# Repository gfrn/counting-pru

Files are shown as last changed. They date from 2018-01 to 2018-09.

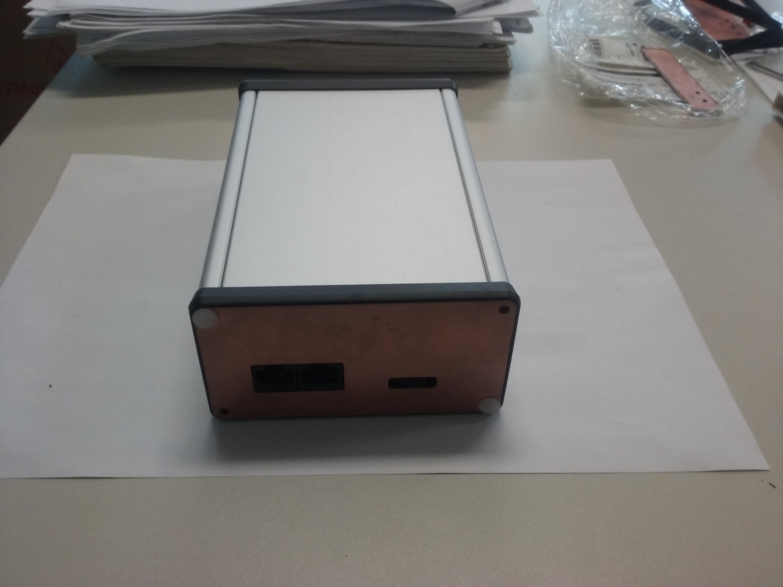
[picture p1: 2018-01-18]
Photos/20171122_133125.jpg

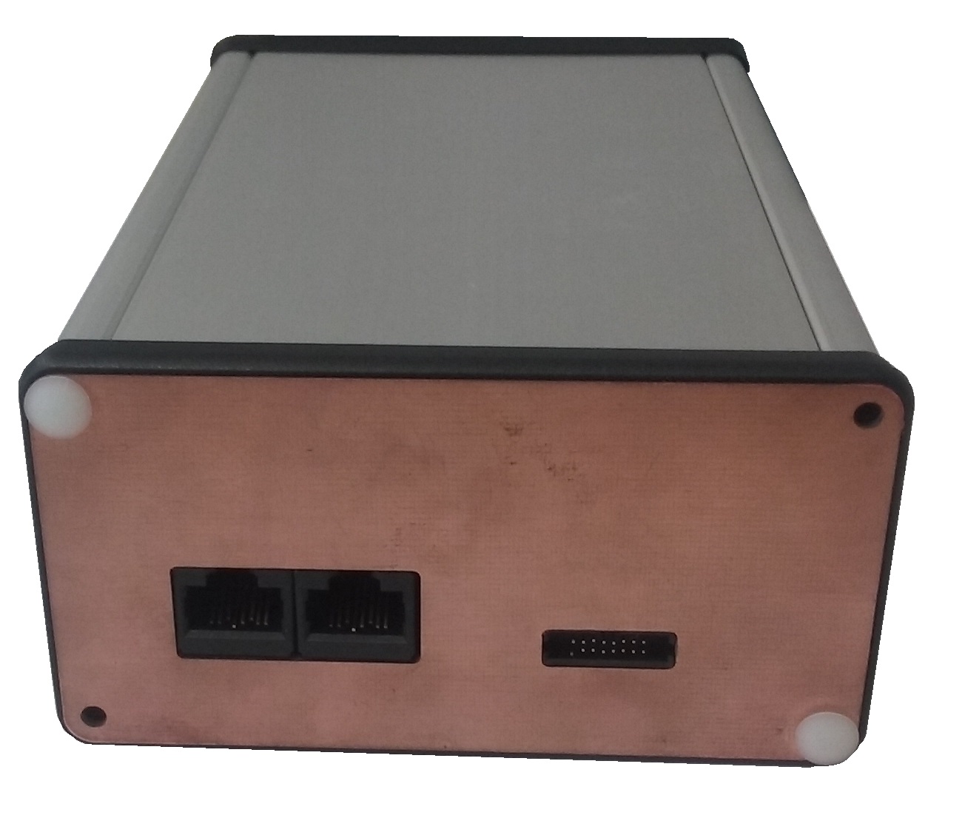
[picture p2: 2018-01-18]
Photos/20171122_133314.jpg

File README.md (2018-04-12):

## CountingPRU - _SIRIUS_
_PRU-based Counters_

Brazilian Synchrotron Light Laboratory (LNLS/CNPEM)
Controls Group

___

_Author:_

Patricia H. Nallin ( _patricia.nallin@lnls.br_ )

_____
_Brief Description:_

Designed as a PRU-based system, this product was developed in order to count trains of pulses during a period of time either from Bergoz Differential BLM or from LNLS Gamma Sensors (4-channel standard TTL signal), up to 14 MHz.

The project consists on:

- Hardware files (Cape board for Beaglebone)
- Library (C or Python)
- EPICS IOC (using 'pcaspy' module)

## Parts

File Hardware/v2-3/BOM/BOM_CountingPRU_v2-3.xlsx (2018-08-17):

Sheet: CountingPRU v2-3
Designator | Description | Value | PartNumber | Package | Manufacturer | Quantity | CNPEM Part Number | OBS | Packaging
Beagle1 | 2x Pin Heander para a BeagleBone Black | BeagleBone | ZW-23-12-F-D-754-178 | 2x Straight_2x23 pitch 2.54mm | SAMTEC | 2 | MT104047 |  | Unit
BR1,BR2 | Bridge Rectifier Single Phase Standard 100V SMD | Diode_Bridge | DF01S-T | RECT_BRIDGE | Diodes Incorporated | 2 | MT107907 |  | Tape
C1 | Aluminum Electrolytic Capacitors Radial SMD 470µF 16V | 470uF | EEE-1CA471UP | CP_Elec_8x5.4 | Panasonic Electronic Components | 1 | AP106777 |  | Tape
C2 | Multilayer Ceramic Capacitors 4.7µF 50V ±10% X7R 1210 SMD | 4.7uF | GRM21BR61E475MA12L | 1210 | Murata | 1 | MT104428 |  | Reel
C27 | Tantalum Capacitor 100uF, 10V, 20%, ESR 0.9ohm | 100uF | TLJT107M010R0900 | 1210 | AVX | 1 | MT103959 |  | Tape
C3,C4 | Ceramic Capacitor SMD ±5% 16V X7R | 1uF | C0805C105J4RACTU | 0805 | AVX | 2 | MT109488 |  | Reel
C30 | Tantalum Capacitor 10uF, 10V, 10%, ESR 3.8ohm | 10uF | 08053C105JAT2A | 1206 | Kemet | 1 | AP111595 |  | Tape
C6 | Ceramic Capacitor 10uF 16V 10% SMD 0805 X5R | 10uF | CL21A106KOQNNNE | 0805 | Samsung ElectroMechanics | 1 | MT104058 |  | Reel
C7,C28,C29 | Multilayer Ceramic Capacitor 100nF 50V 5% SMD 0805 X7R | 100nF | GCM21BR72A104KA37L | 0805 | Murata | 3 | MT114854 |  | Reel
C8,C5,C9,C10 | Ceramic Capacitor 33pF 50V 10% SMD 0805 C0G/NP0 | 33pF | 08055A330JAT2A | 0805 | AVX | 4 | MT112460 |  | Reel
D1 | LED Circuit Board Indicator Single Red Diffused, Through Hole, Right Angle 2V 20mA 90° | LED-Red | WP934CB/ID | 2x1 PTH pitch 2,54mm | Kingbright | 1 | AP110389 |  | Unit
D9,D11 | Diode Schottky 40V 750mA (DC) Surface Mount | Schottky | BAT165E6327HTSA1 | SOD-323 | Infineon Technologies | 2 | MT104048 |  | Tape
D10,D12 | Red LED, 2V, 20mA, SMD 0805 | LED Red | LTST-C171KRKT | 0805 | Lite-On Inc | 2 | AP111653 |  | Reel
J1,J2,J3,J4 | RJ45 Jack Connector Right Angle | RJ45 | SS-60000-010 | RJ45-STEWART | Stewart | 4 | MT107916 |  | Tube
JP1 | DIP Switch SMD 1 position | Dip Switch 1 pos | KAE01SGGT | DIP Switch SMD 1 position | E-Switch | 1 | MT104049 |  | Tube
P1,P2 | Connector 90° PTH 02x08 | CONN_02X08 | 3221-16-0200-00 | 2x08_PTH_Pitch1.27mm | CNC Tech | 2 | MT107378 |  | Unit
Q3,Q2,Q1 | Bipolar (BJT) Transistor NPN SMD 40V 800mA 300MHz 350mW | BSR14 | BSR14 | SOT-23 | Fairchild Semiconductor | 3 | MT104051 |  | Tape
R11,R12 | Resistor SMD 100Ω ±1% 1W Thin Film | 100 | MMB02070C1000FB200 | MELF 0207 | Vishay | 2 | MT112459 |  | Reel
R13,R14 | Resistor SMD 120 Ω ±1% 0.125W Thick Film | 120 | 0805W8F1200T5E | 0805 | RoyalOhm | 2 | MT115760 |  | Reel
R16 | Resistor SMD 620Ω ±1% 0.125W Thick Film | 620 | RK73H2ATTD6200F | 0805 | KOA Speer | 1 | MT109494 |  | Reel
R17 | Resistor SMD 180 ohm 1% 1/8W Thin Film | 180 | 0805W8F1800T5E | 0805 | RoyalOhm | 1 | MT114496 |  | Reel
R18,R5,R6 | Resistor SMD 1K ohm 1% 1/8W Thick Film | 1k | 0805W8F1001T5E | 0805 | RoyalOhm | 3 | MT109492 |  | Reel
R19,R20,R21,R22,R27,R30,R31 | Resistor SMD 10 kΩ ±1% 0.125W Thick Film | 10k | 0805W8F1002T5E | 0805 | RoyalOhm | 7 | MT109485 |  | Reel
R23,R2,R1,R24 | Resistor SMD 0 Ohms 0.125W Thick Film | 0 | RC0805JR-070RL | 0805 | Yageo | 4 | MT100803 | NÃO DEVEM SER MONTADOS | NÃO SERÁ FORNECIDO
R25 | Resistor 910K ohm 1% 1/8W SMD 0805 Thick Film | 910KΩ | 0805W8F9103T5E | 0805 | RoyalOhm | 1 | MT115761 |  | Reel
R26,R29 | Resistor 330 ohm, 1/8W, SMD 0805, Thick Film | 330Ω | 0805W8F3300T5E | 0805 | RoyalOhm | 2 | MT115762 |  | Reel
R28 | Resistor 220K ohm 1% 1/8W SMD 0805 Thick Film | 220kΩ | 0805W8F2203T5E | 0805 | RoyalOhm | 1 | MT115763 |  | Reel
R3,R4 | Resistor SMD 100Ω ±1% 0.125W Thick Film | 100 | RK73H2ATTD1000F | 0805 | KOA Speer | 2 | MT115765 |  | Reel
R7,R8,R9,R10, R15 | Resistor SMD 4.7 kΩ ±1% 0.125W Thick Film | 4k7 | 0805W8F4701T5E | 0805 | RoyalOhm | 4 | MT115764 |  | Reel
T1 | Module XFRMR LAN 10/100 PoE SMD | Module-XFRMR-POE | S558-5500-25-F | Module-XFRMR-Poe | Bel Fuse Inc. | 1 | MT107908 |  | Tape
T2,T3 | 2 Line Common Mode Choke Surface Mount 500 Ohm @ 100MHz 4A DCR 27 mOhm | Transformer_1P_1S | DLW5BTM501SQ2L | Horizontal, 6 PC Pad | Murata | 2 | MT109675 |  | Tape
U1,U2,U3,U4,U5,U6,U23,U24 | Single D-type Flip-flop | 741G74 | 296-25554-2-ND | TSSOP-8 | Texas Instruments | 8 | AP105702 |  | Tape
U14,U15,U20 | 2 Circuit IC Switch 1:1 1Ω US8 | TS5A21366 | TS5A21366DCUR | VSSOP-8 | Texas Instruments | 3 | AP109801 |  | Tape
U16 | Isolated PoE module Output 5V – 13W | Ag9200 | AG9205S | 9200-Silvertel | Silvertel | 1 | MT107905 |  | Unit
U17 | Isolated Module DC DC Converter 5V→5V 200mA 1W | VIBLSD1-S5-S5-DIP | VIBLSD1-S5-S5-DIP | 14-DIP-5 Leads | CUI Inc. | 1 | MT108027 |  | Tube
U18 | Isolated Module DC DC Converter 5V→±12V 42mA 1W | MEV1D0512DC | MEV1D0512DC | 14-DIP-6 Leads | Murata Power Solutions Inc. | 1 | MT108008 |  | Tube
U19,U22 | IC Single 2-input AND Gate SMD SOT-353 | 1G08 | 74AHC1G08SE-7 | SOT-353 | Diodes Inc | 2 | MT104245 |  | Reel
U21 | IC 74HC123 SMD SOIC-16 | 74HC123 | 74HC123D | SOIC-16 | NXP Semiconductors | 1 | AP111593 |  | Tape
U7,U12,U13 | Buffer Inverting 1 channel SMD | 1G04 | 74AHC1G04SE-7 | SOT-353 | Diodes Inc | 3 | MT104246 |  | Reel
U8,U9,U10,U11,U25,U26 | Buffer Non-Inverting Push-Pull Output | 1G125 | 74AHC1G125SE-7 | SOT-353 | Nexperia Inc | 6 | MT103958 |  | Reel

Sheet: Montagem mecânica
Designator | Description | Value | PartNumber | Package | Manufacturer | Quantity | CNPEM Part Number | OBS | Packaging
N/A | Cabo modular macho-macho 8P8C (RJ45,ETHERNET) | N/A | DK-1511-001/BL | N/A | Assmann WSW Components | 1 | MT107917 |  | Unit
 | CAIXA DE ALUMINIO 159.99MM X 130.00MM X 53.00MM, TAMANHO EUROCARD |  | 1455N1601 |  | Hammond Manuf. | 1 | AP110391 |  | Unit

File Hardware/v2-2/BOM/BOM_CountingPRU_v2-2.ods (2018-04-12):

Designator | Description | Value | PartNumber | Package | Manufacturer | Quantity | CNPEM Part Number | OBS | Qtty 120 placas
Beagle1 | 2x Pin Heander para a BeagleBone Black | BeagleBone | ZW-23-12-F-D-754-178 | 2x Straight_2x23 pitch 2.54mm | SAMTEC | 2 | MT104047 |  | 240
BR1,BR2 | Bridge Rectifier Single Phase Standard 100V SMD | Diode_Bridge | DF01S-T | RECT_BRIDGE | Diodes Incorporated | 2 | MT107907 |  | 240
C1 | Aluminum Electrolytic Capacitors Radial SMD 470µF 16V | 470uF | EEE-1CA471UP | CP_Elec_8x5.4 | Panasonic Electronic Components | 1 | AP106777 |  | 120
C2 | Multilayer Ceramic Capacitors 4.7µF 50V ±10% X7R 1210 SMD | 4.7uF | GRM21BR61E475MA12L | 1210 | Murata | 1 | MT104428 |  | 120
C3,C4 | Ceramic Capacitor SMD ±5% 16V X7R | 1uF | C0805C105J4RACTU | 0805 | Kemet | 2 | MT104060 |  | 240
C6 | Ceramic Capacitor 10uF 16V 10% SMD 0805 X5R | 10uF | CL21A106KOQNNNE | 0805 | Samsung ElectroMechanics | 1 | MT104058 |  | 120
C7,C28,C29 | Multilayer Ceramic Capacitor 100nF 50V 5% SMD 0805 X7R | 100nF | 08055C104JAT2A | 0805 | AVX | 3 | MT104382 |  | 360
C8,C5,C9,C10 | Ceramic Capacitor 33pF 50V 10% SMD 0805 C0G/NP0 | 33pF | 08055A330JAT2A | 0805 | AVX | 4 | MT112460 |  | 480
C27 | Tantalum Capacitor 100uF, 10V, 20%, ESR 0.9ohm | 100uF | TLJT107M010R0900 | 1210 | AVX | 1 | MT103959 |  | 120
C30 | Tantalum Capacitor 10uF, 10V, 10%, ESR 3.8ohm | 10uF | T491A106K010AT7280 | 1206 | Kemet | 1 | AP111595 |  | 120
D1 | LED Circuit Board Indicator Single Red Diffused, Through Hole, Right Angle 2V 20mA 90° | LED-Red | WP934CB/ID | 2x1 PTH pitch 2,54mm | Kingbright | 1 | AP110389 |  | 120
J1,J2,J3,J4 | RJ45 Jack Connector Right Angle | RJ45 | SS-60000-010 | RJ45-STEWART | Stewart | 4 | MT107916 |  | 480
P1,P2 | Connector 90° PTH 02x08 | CONN_02X08 | 3221-16-0200-00 | 2x08_PTH_Pitch1.27mm | CNC Tech | 2 | MT107378 |  | 240
Q3,Q2,Q1 | Bipolar (BJT) Transistor NPN SMD 40V 800mA 300MHz 350mW | BSR14 | BSR14 | SOT-23 | Fairchild Semiconductor | 3 | MT104051 |  | 360
R11,R12 | Resistor SMD 100Ω ±1% 1W Thin Film | 100 | MMB02070C1000FB200 | MELF 0207 | Vishay | 2 | MT112459 |  | 240
R13,R14 | Resistor SMD 120 Ω ±1% 0.125W Thick Film | 120 | RC0805FR-07120RL | 0805 | Yageo | 2 | MT104234 |  | 240
R16 | Resistor SMD 620Ω ±1% 0.125W Thick Film | 620 | RC0805FR-07620RL | 0805 | Yageo | 1 | MT104227 |  | 120
R17 | Resistor SMD 150 ohm 1% 1/8W Thin Film | 150 | RC0805FR-07150RL | 0805 | Yageo | 1 | MT104053 |  | 120
R18,R5,R6 | Resistor SMD 1K ohm 1% 1/8W Thick Film | 1k | RC0805FR-071KL | 0805 | Yageo | 3 | MT104228 |  | 360
R19,R20,R21,R22,R27,R30,R31 | Resistor SMD 10 kΩ ±1% 0.125W Thick Film | 10k | RC0805FR-0710K | 0805 | Yageo | 7 | MT104235 |  | 840
R23,R2,R1,R24 | Resistor SMD 0 Ohms 0.125W Thick Film | 0 | RC0805JR-070RL | 0805 | Yageo | 4 | MT100803 | NÃO DEVEM SER MONTADOS | 0
R3,R4 | Resistor SMD 100Ω ±1% 0.125W Thick Film | 100 | RC0805FR-07100RL | 0805 | Yageo | 2 | MT104236 |  | 240
R7,R8,R9,R10, R15 | Resistor SMD 4.7 kΩ ±1% 0.125W Thick Film | 4k7 | RC0805FR-074K7L | 0805 | Yageo | 4 | MT104433 |  | 480
T1 | Module XFRMR LAN 10/100 PoE SMD | Module-XFRMR-POE | S558-5500-25-F | Module-XFRMR-Poe | Bel Fuse Inc. | 1 | MT107908 |  | 120
T2,T3 | 2 Line Common Mode Choke Surface Mount 500 Ohm @ 100MHz 4A DCR 27 mOhm | Transformer_1P_1S | DLW5BTM501SQ2L | Horizontal, 6 PC Pad | Murata | 2 | MT109675 |  | 240
U1,U2,U3,U4,U5,U6,U23,U24 | Single D-type Flip-flop | 741G74 | 296-25554-2-ND | TSSOP-8 | Texas Instruments | 8 | AP105702 |  | 960
U14,U15,U20 | 2 Circuit IC Switch 1:1 1Ω US8 | TS5A21366 | TS5A21366DCUR | VSSOP-8 | Texas Instruments | 3 | AP109801 |  | 360
U16 | Isolated PoE module Output 5V – 13W | Ag9200 | AG9205S | 9200-Silvertel | Silvertel | 1 | MT107905 |  | 120
U17 | Isolated Module DC DC Converter 5V→5V 200mA 1W | VIBLSD1-S5-S5-DIP | VIBLSD1-S5-S5-DIP | 14-DIP-5 Leads | CUI Inc. | 1 | MT108027 |  | 120
U18 | Isolated Module DC DC Converter 5V→±12V 42mA 1W | MEV1D0512DC | MEV1D0512DC | 14-DIP-6 Leads | Murata Power Solutions Inc. | 1 | MT108008 |  | 120
U7,U12,U13 | Buffer Inverting 1 channel SMD | 1G04 | 74AHC1G04SE-7 | SOT-353 | Diodes Inc | 3 | MT104246 |  | 360
U8,U9,U10,U11,U25,U26 | Buffer Non-Inverting Push-Pull Output | 1G125 | 74AHC1G125SE-7 | SOT-353 | Diodes Inc | 6 | MT103958 |  | 720
U19,U22 | IC Single 2-input AND Gate SMD SOT-353 | 1G08 | 74AHC1G08SE-7 | SOT-353 | Diodes Inc | 2 | MT104245 |  | 240
D9,D11 | Diode Schottky 40V 750mA (DC) Surface Mount | Schottky | BAT165E6327HTSA1 | SOD-323 | Infineon Technologies | 2 | MT104048 |  | 240
R25 | Resistor 910K ohm 1% 1/8W SMD 0805 Thick Film | 910KΩ | RC0805FR-07910KL | 0805 | Yageo | 1 | MT104231 |  | 120
R26,R29 | Resistor 330 ohm, 1/8W, SMD 0805, Thick Film | 330Ω | RC0805FR-07330RL | 0805 | Yageo | 2 | MT104229 |  | 240
R28 | Resistor 220K ohm 1% 1/8W SMD 0805 Thick Film | 220kΩ | RC0805FR-07220KL | 0805 | Yageo | 1 | MT104232 |  | 120
U21 | IC 74HC123 SMD SOIC-16 | 74HC123 | 74HC123D | SOIC-16 | NXP Semiconductors | 1 | AP111593 |  | 120
JP1 | DIP Switch SMD 1 position | Dip Switch 1 pos | KAE01SGGT | DIP Switch SMD 1 position | E-Switch | 1 | MT104049 |  | 120
D9,D11 | Red LED, 2V, 20mA, SMD 0805 | LED Red | LTST-C171KRKT | 0805 | Lite-On Inc | 2 | AP111653 |  | 240

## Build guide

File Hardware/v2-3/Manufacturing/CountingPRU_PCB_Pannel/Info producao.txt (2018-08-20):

Informações para produção:

O modelo "CountingPRU_v2-3_Gerber" deve ser produzido conforme o arquivo de panelização "PN-COUNTINGPRU V2.3.PCB"

Dimensões da PCI: 100,0x160,0mm

Dimensões do painel: 203,0x180,0mm

Quantidade pçs/painel: 02pçs

Maretial: PCI Dupla face fibra 1,6mm 1Oz.

Wagner Luiz de Paula
wagner@arossat.com.br
www.arossat.com.br
11 - 5666 4858

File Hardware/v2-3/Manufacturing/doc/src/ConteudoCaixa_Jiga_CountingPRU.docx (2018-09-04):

Jiga de Testes

“CountingPRU v2.3”

Júlia Giatti Hidalgo | Patrícia Henriques Nallin
Grupo de Controle - LNLS

julia.hidalgo@lnls.br | patricia.nallin@lnls.br
(19) 3512 1195

Jiga de Testes Para a Placa de Circuito Impresso

“CountingPRU v2.3”

# Conteúdo desta caixa

- 4 cabos Ethernet 30cm
- 2 cabos IDC/BNC fêmea
- 2 cabos SMA/BNC
- 1 caixa Oscilador 3.2kHz
- 1 caixa oscilador 1,5kHz
- 2 Beaglebone Black modelo Jiga CountingPRU (1 reserva)
- 2 caixas Bergoz
- 2 fontes de alimentação DC 5V/2,5A
- 1 Injetor POE modelo CNPEM
- Manual Jiga de Testes

Estes itens devem permanecer organizados.

Em caso de dúvidas, contactar:

Júlia Giatti Hidalgo | Patrícia Henriques Nallin
Grupo de Controle - LNLS

julia.hidalgo@lnls.br | patricia.nallin@lnls.br
(19) 3512 1195

v1.0

Agosto/2018

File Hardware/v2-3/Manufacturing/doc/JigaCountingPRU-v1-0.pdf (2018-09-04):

# Jiga de Testes Para a Placa de Circuito Impresso “CountingPRU v2.3”

Júlia Giatti Hidalgo
Grupo de Controle - LNLS
Julia.hidalgo@lnls.br
(19) 3512 1195

v1.0

Agosto/2018

## 1. CONTROLE DE VERSÃO

Versão | Data | Responsável | Observações
1.0 | Agosto/2018 | Júlia Giatti Hidalgo | Primeira versão do documento

## 2. Sumário

### 1. CONTROLE DE VERSÃO | 3

### 2. Sumário | 5

### 3. MATERIAIS NECESSÁRIOS | 7

### 4. SEQUÊNCIA DE OPERAÇÕES | 7

### 5. DETALHAMENTO DOS TESTES | 7

## 3. MATERIAIS NECESSÁRIOS

■ | 4 cabos Ethernet
■ | 2 cabos IDC/BNC fêmea
■ | 2 cabos SMA/BNC
■ | 1 caixa Oscilador 3.2kHz
■ | 1 caixa oscilador 1,5kHz
■ | 1 Beaglebone Black modelo Jiga CountingPRU
■ | 2 caixas Bergoz
■ | 2 fontes de alimentação DC 5V/2,5A
■ | 1 Injetor POE modelo CNPEM
| O CNPEM/LNLS fornecerá os itens descritos acima para a realização dos testes funcionais.

## 4. SEQUÊNCIA DE OPERAÇÕES

Para a realização e validação dos testes funcionais, uma sequência de operação deve ser feita e contém os seguintes passos:

Conectar e alimentar o sistema
Testes funcionais

## 5. DETALHAMENTO DOS TESTES

Para a realização e validação dos testes funcionais, uma sequência de operação deve ser feita e contém os seguintes passos:

### 1. Conectar e alimentar o sistema

(a) Conecte os cabos IDC/BNC fêmea na placa, conforme imagem abaixo.

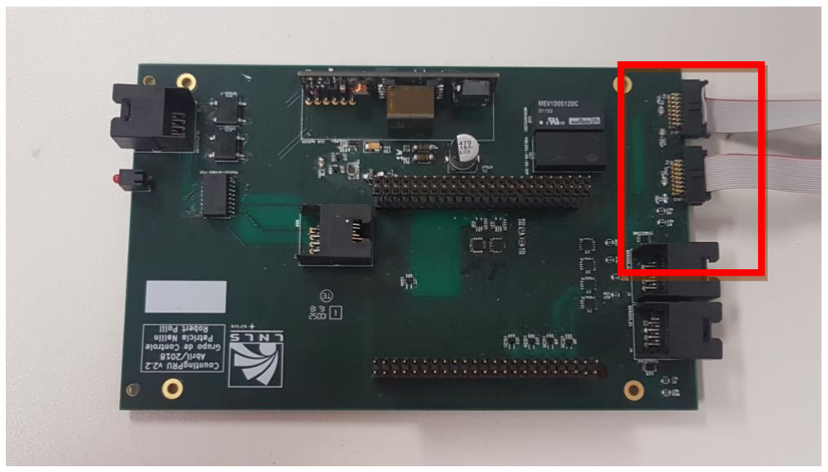
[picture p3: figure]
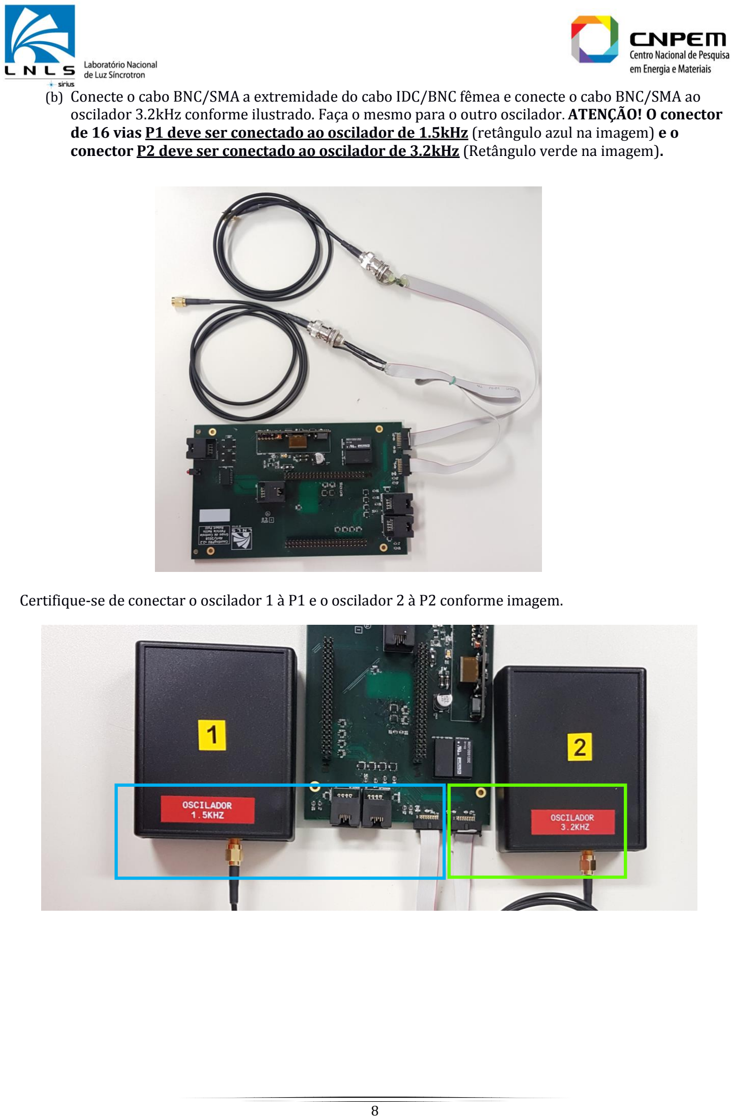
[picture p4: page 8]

(b) Conecte o cabo BNC/SMA a extremidade do cabo IDC/BNC fêmea e conecte o cabo BNC/SMA ao oscilador 3.2kHz conforme ilustrado. Faça o mesmo para o outro oscilador. ATENÇÃO! O conector de 16 vias P1 deve ser conectado ao oscilador de 1.5kHz (retângulo azul na imagem) e o conector P2 deve ser conectado ao oscilador de 3.2kHz (Retângulo verde na imagem).

Certifique-se de conectar o oscilador 1 à P1 e o oscilador 2 à P2 conforme imagem.

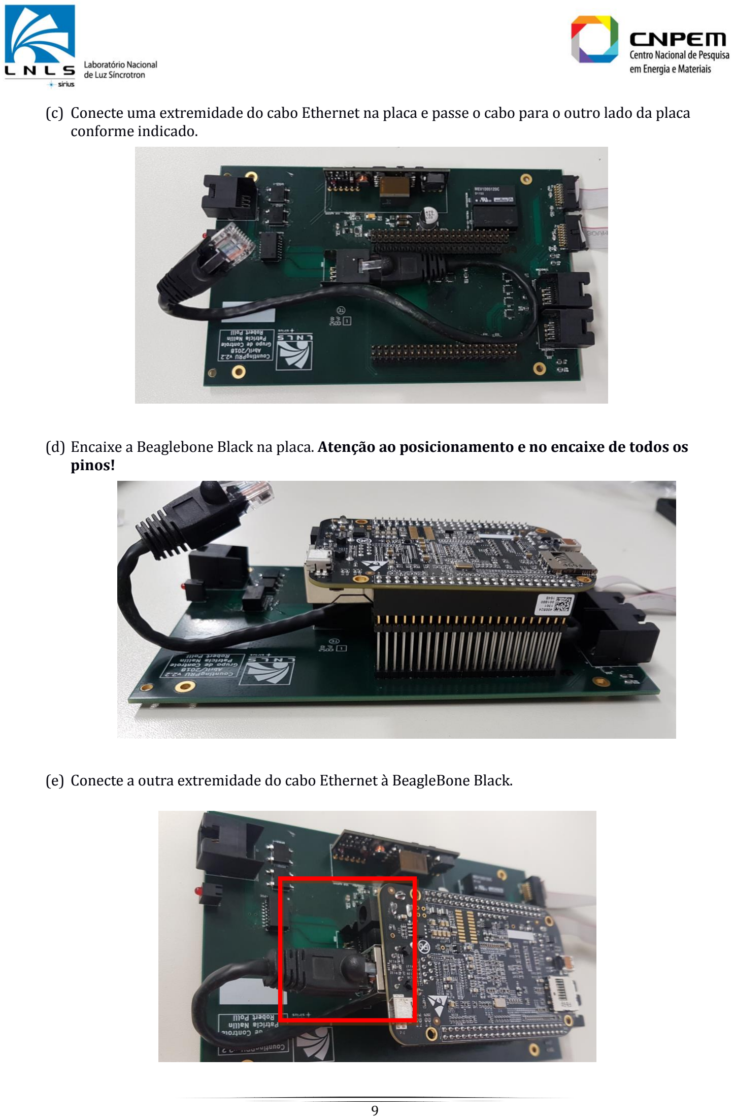
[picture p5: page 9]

(c) Conecte uma extremidade do cabo Ethernet na placa e passe o cabo para o outro lado da placa conforme indicado.
(d) Encaixe a Beaglebone Black na placa. Atenção ao posicionamento e no encaixe de todos os pinos!
(e) Conecte a outra extremidade do cabo Ethernet à BeagleBone Black.

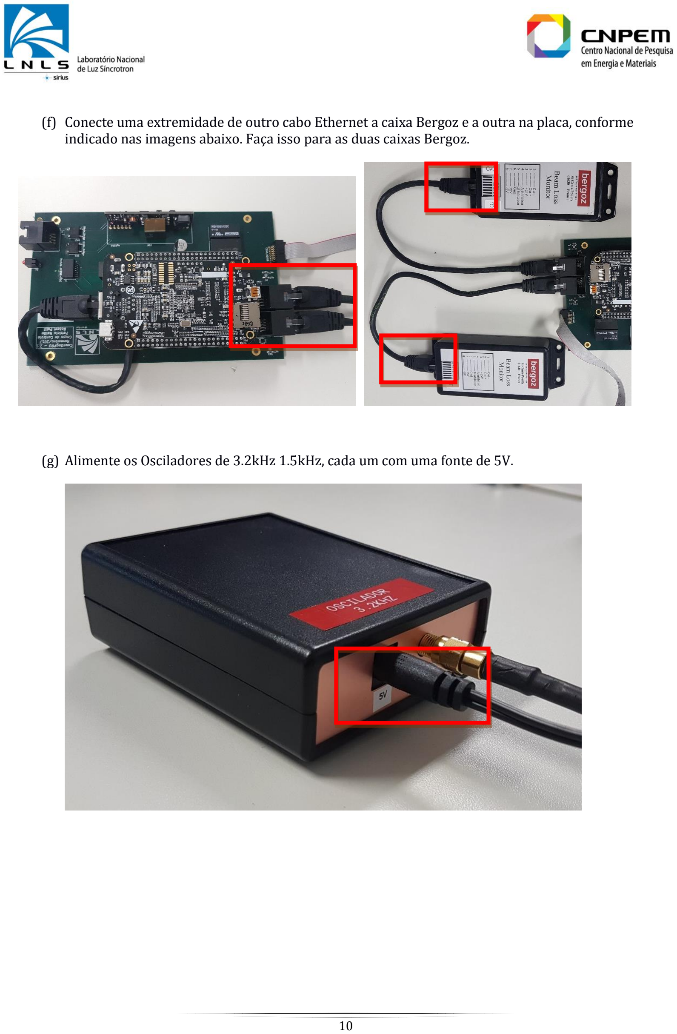
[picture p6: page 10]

(f) Conecte uma extremidade de outro cabo Ethernet a caixa Bergoz e a outra na placa, conforme indicado nas imagens abaixo. Faça isso para as duas caixas Bergoz.
(g) Alimente os Osciladores de 3.2kHz 1.5kHz, cada um com uma fonte de 5V.

(h) Ligue o módulo injetor POE à tomada e conecte o cabo ethernet na porta disponível (porta PoE).

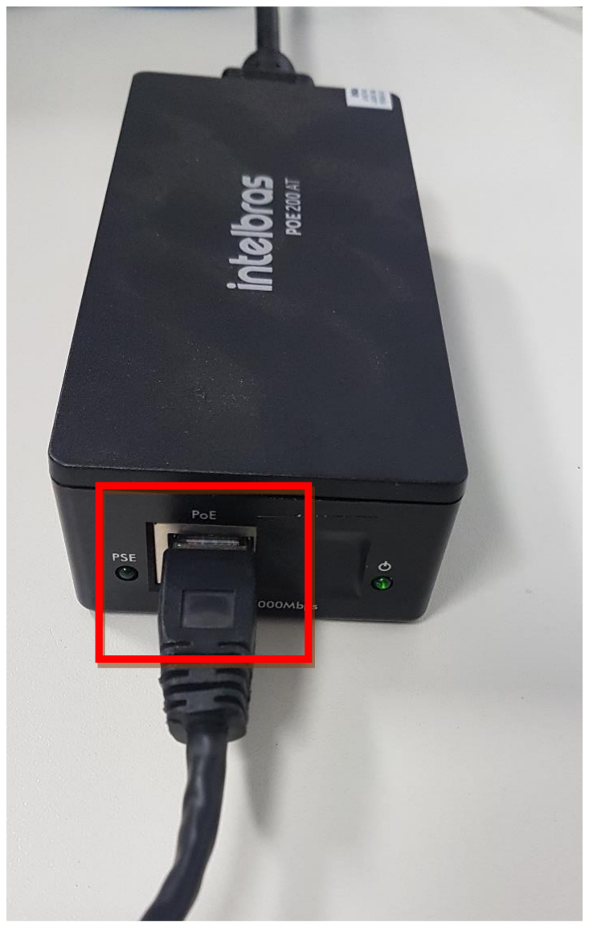
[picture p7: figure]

### 2. Testes Funcionais

(a) Alimente a placa através da outra ponta do cabo Ethernet conectado ao módulo Poe.

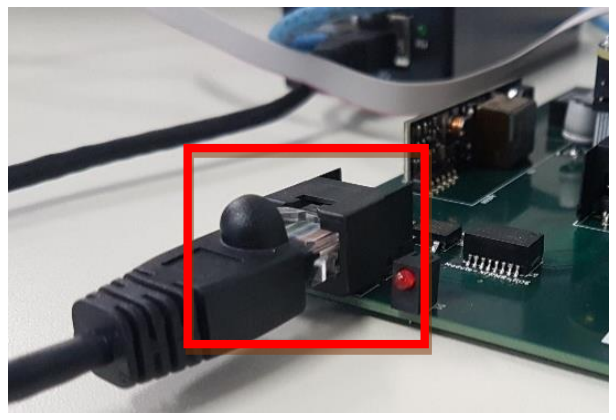
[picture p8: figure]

(b) Verifique que os LEDs azuis da Beaglebone Black acenderam, localizados próximos a entrada Ethernet dela.

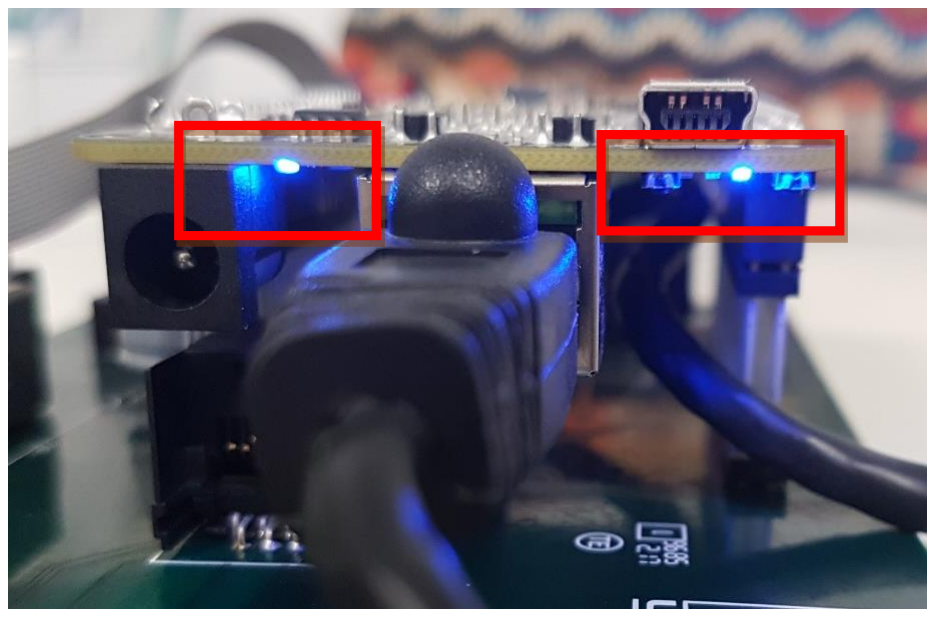
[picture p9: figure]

(c) Aguarde até que o LED vermelho na borda da placa acenda.

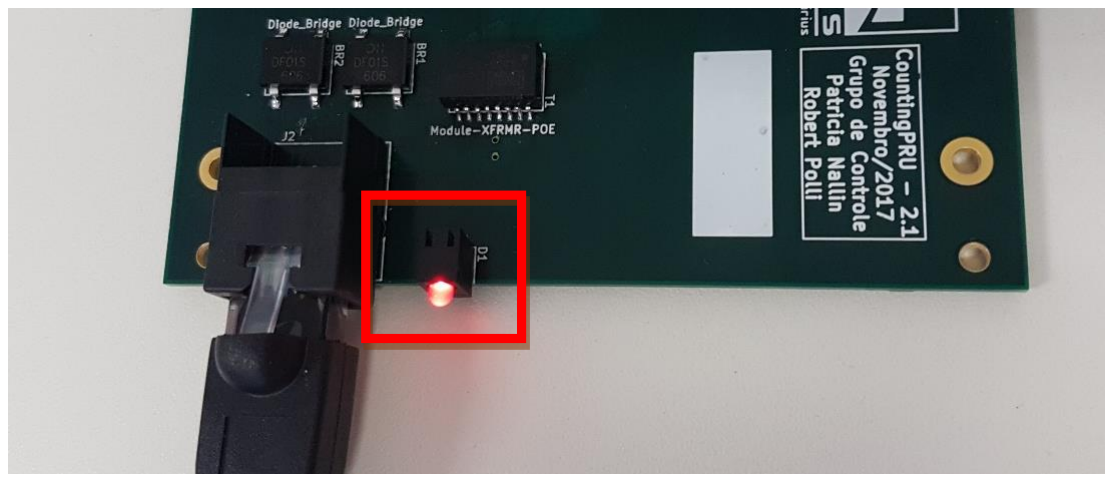
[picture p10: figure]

(d) Logo após alimentar a placa, o LED vermelho começará a piscar indicando o resultado de cada teste.
(e) Teste Bem Sucedido
Para um teste bem sucedido, decorre-se um certo intervalo de tempo e o LED deve piscar duas vezes rapidamente. Novamente, deve-se ocorrer um intervalo de tempo e o LED deve piscar duas vezes rapidamente e depois permanecer ligado.

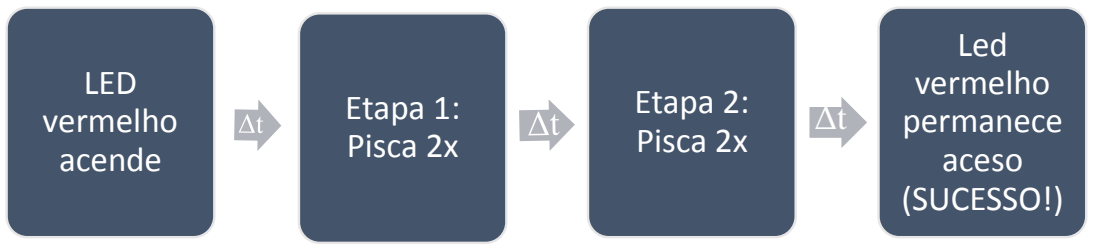
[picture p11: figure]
LED vermelho acende; Etapa 1: Pisca 2x; Etapa 2: Pisca 2x; Led vermelho permanece aceso (SUCESSO!)

## LED vermelho

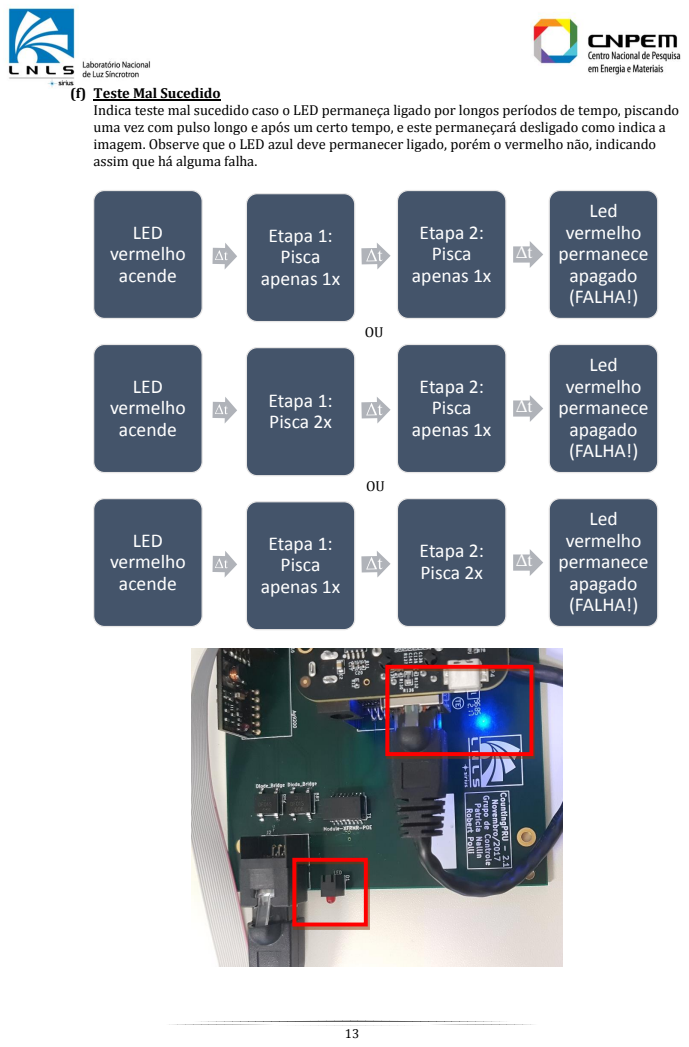
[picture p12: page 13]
acende; Etapa 1: Pisca apenas 1x; Etapa 2: Pisca apenas 1x; Led vermelho permanece apagado (FALHA!); LED vermelho acende; Etapa 1: Pisca 2x; Etapa 2: Pisca 2x

(f) Teste Mal Sucedido
Indica teste mal sucedido caso o LED permaneça ligado por longos períodos de tempo, piscando
uma vez com pulso longo e após um certo tempo, e este permaneçará desligado como indica a
imagem. Observe que o LED azul deve permanecer ligado, porém o vermelho não, indicando
assim que há alguma falha.

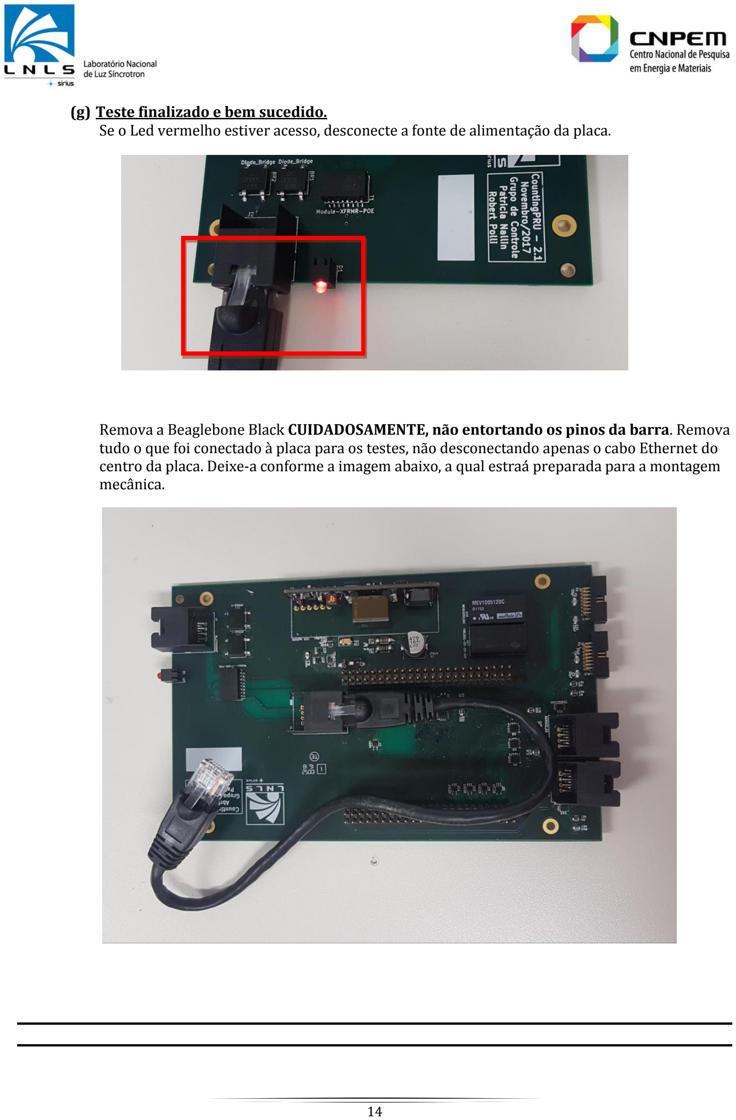
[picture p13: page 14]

(g) Teste finalizado e bem sucedido.
Se o Led vermelho estiver acesso, desconecte a fonte de alimentação da placa.

Remova a Beaglebone Black CUIDADOSAMENTE, não entortando os pinos da barra. Remova tudo o que foi conectado à placa para os testes, não desconectando apenas o cabo Ethernet do centro da placa. Deixe-a conforme a imagem abaixo, a qual estraá preparada para a montagem mecânica.

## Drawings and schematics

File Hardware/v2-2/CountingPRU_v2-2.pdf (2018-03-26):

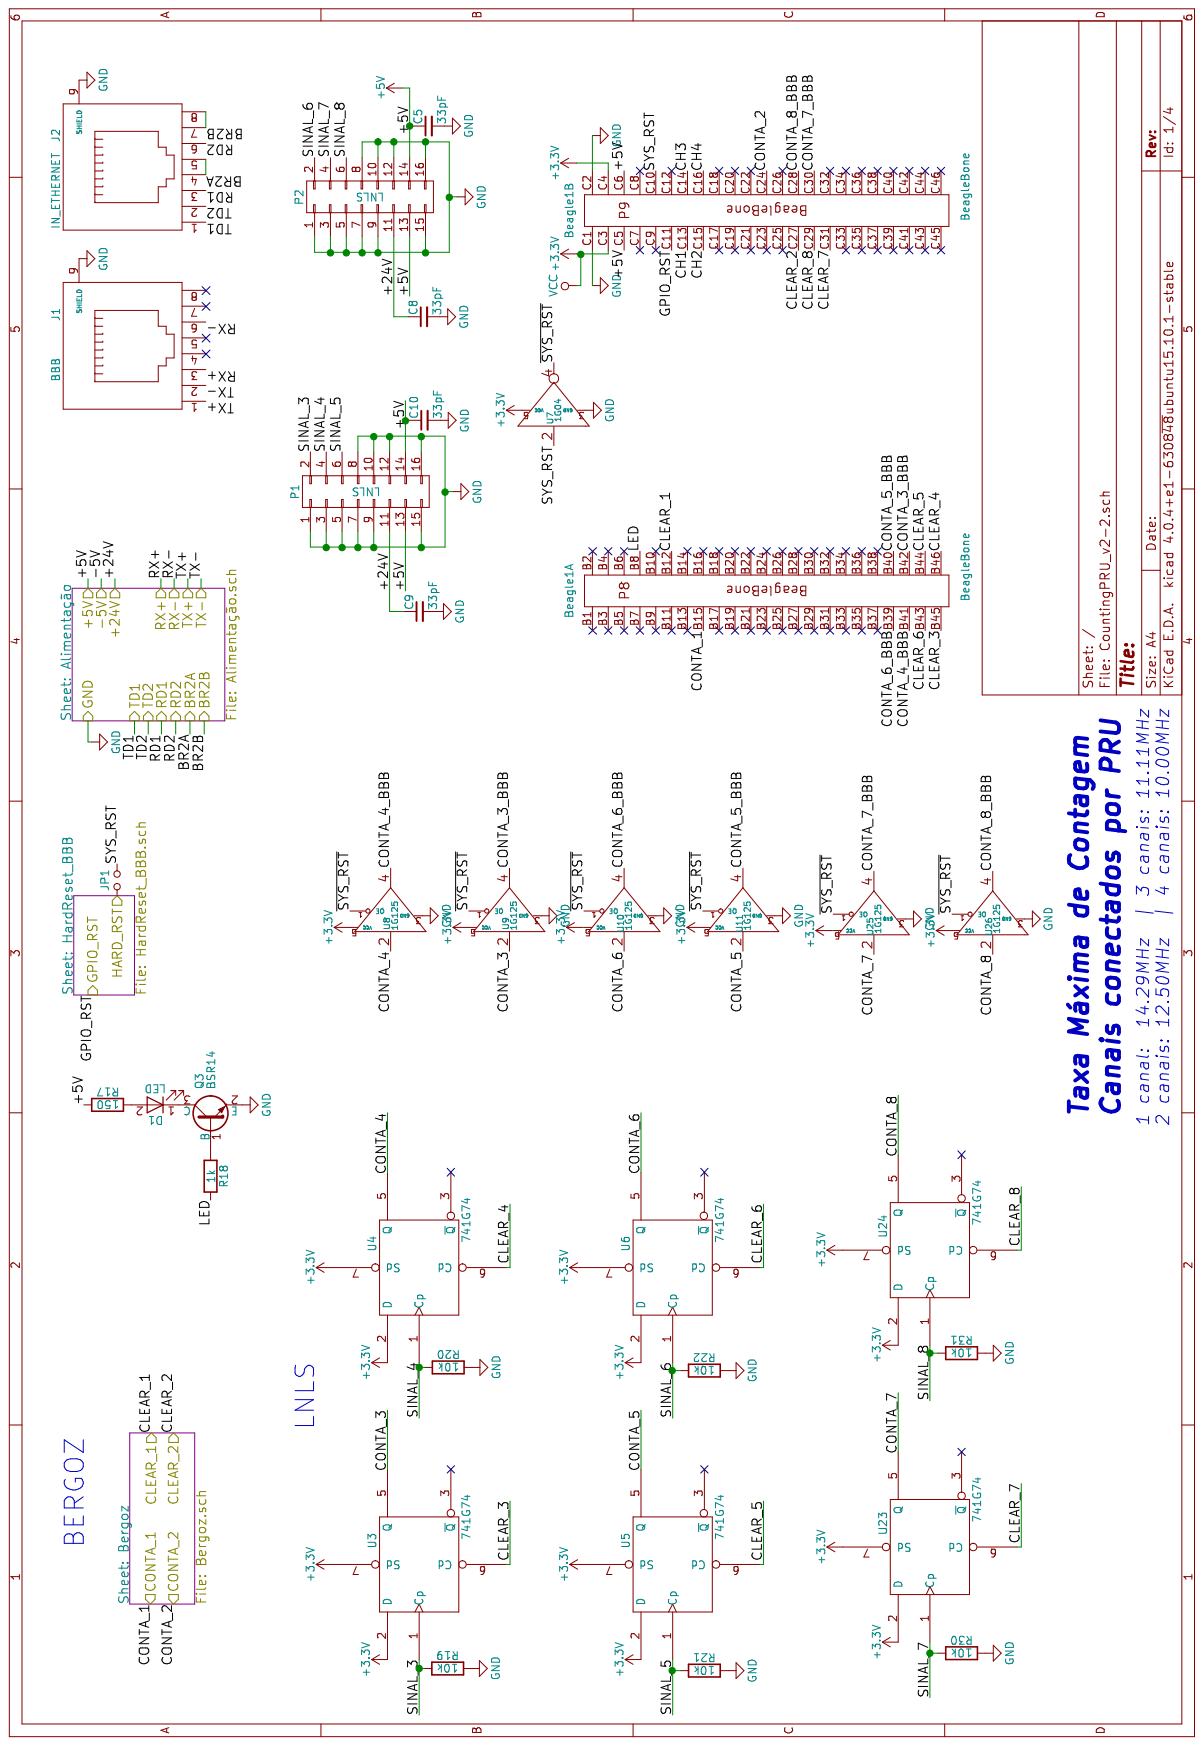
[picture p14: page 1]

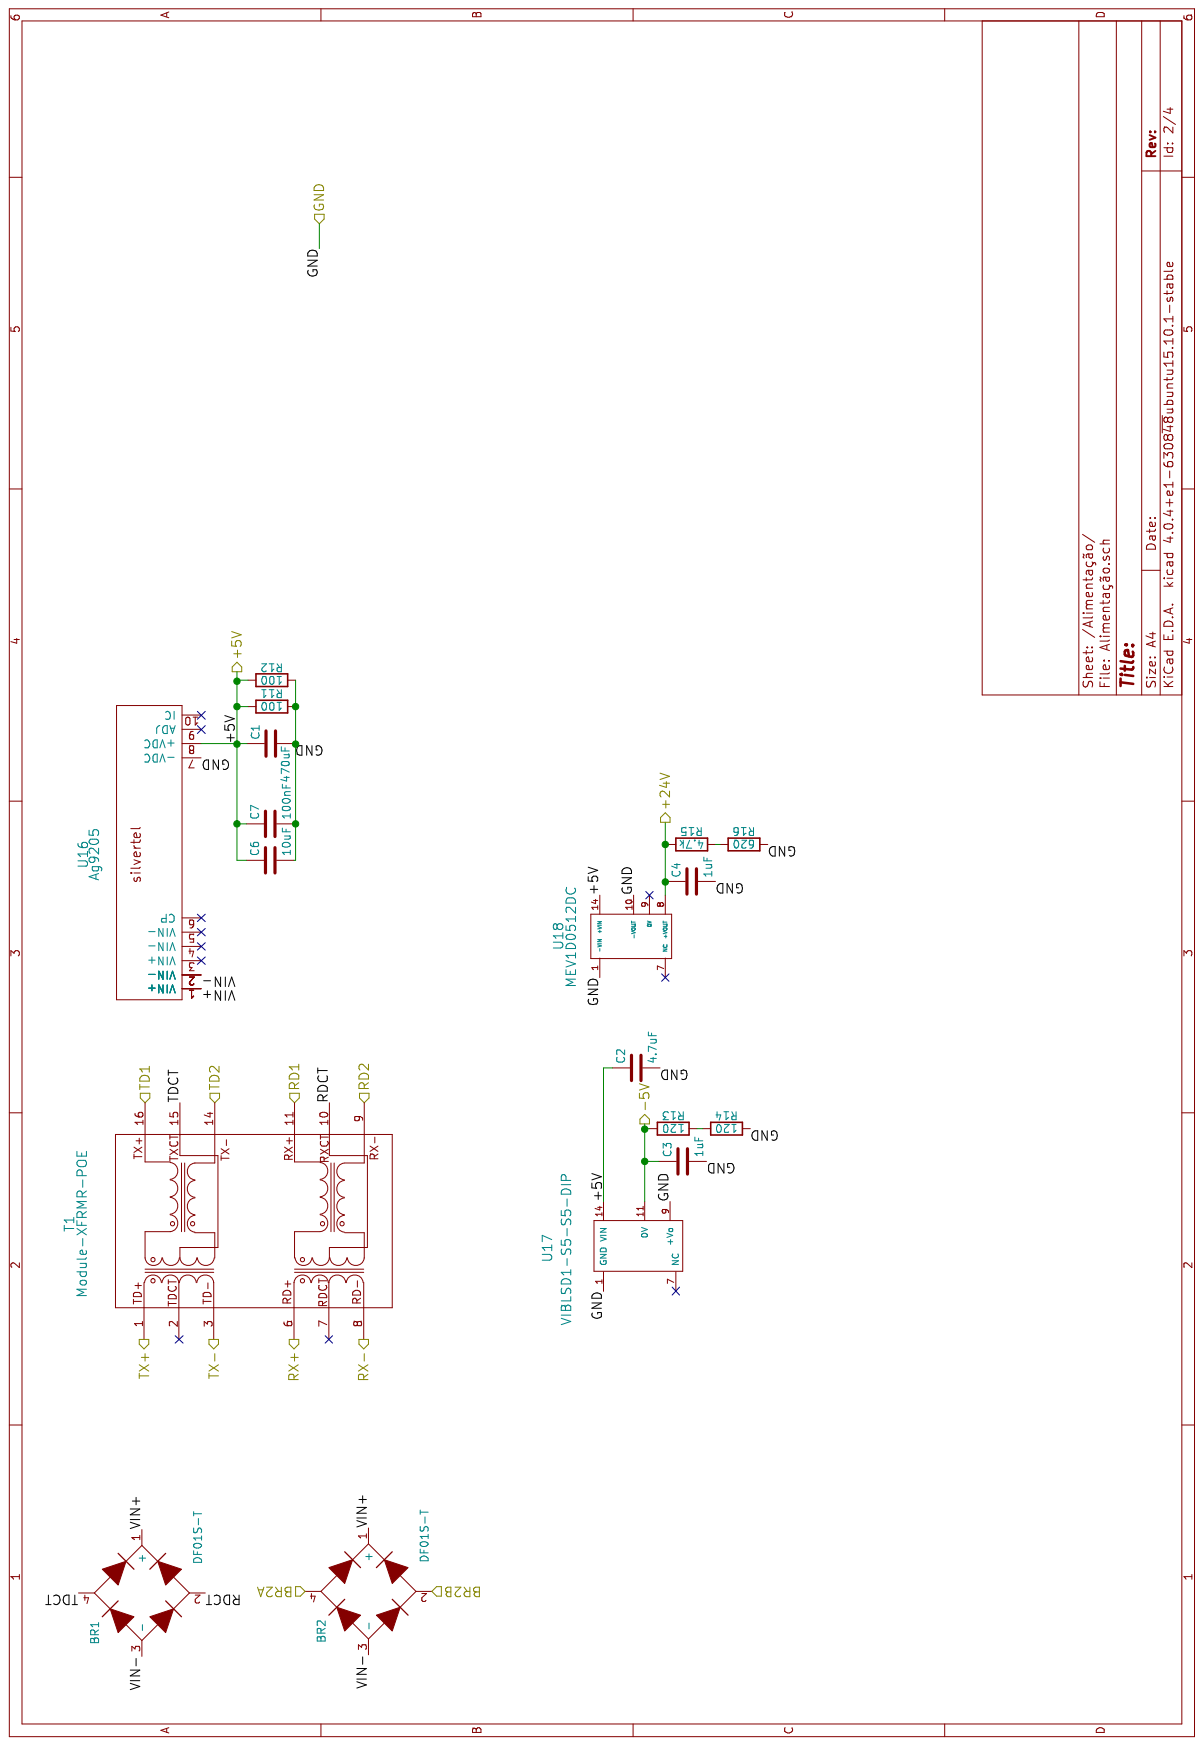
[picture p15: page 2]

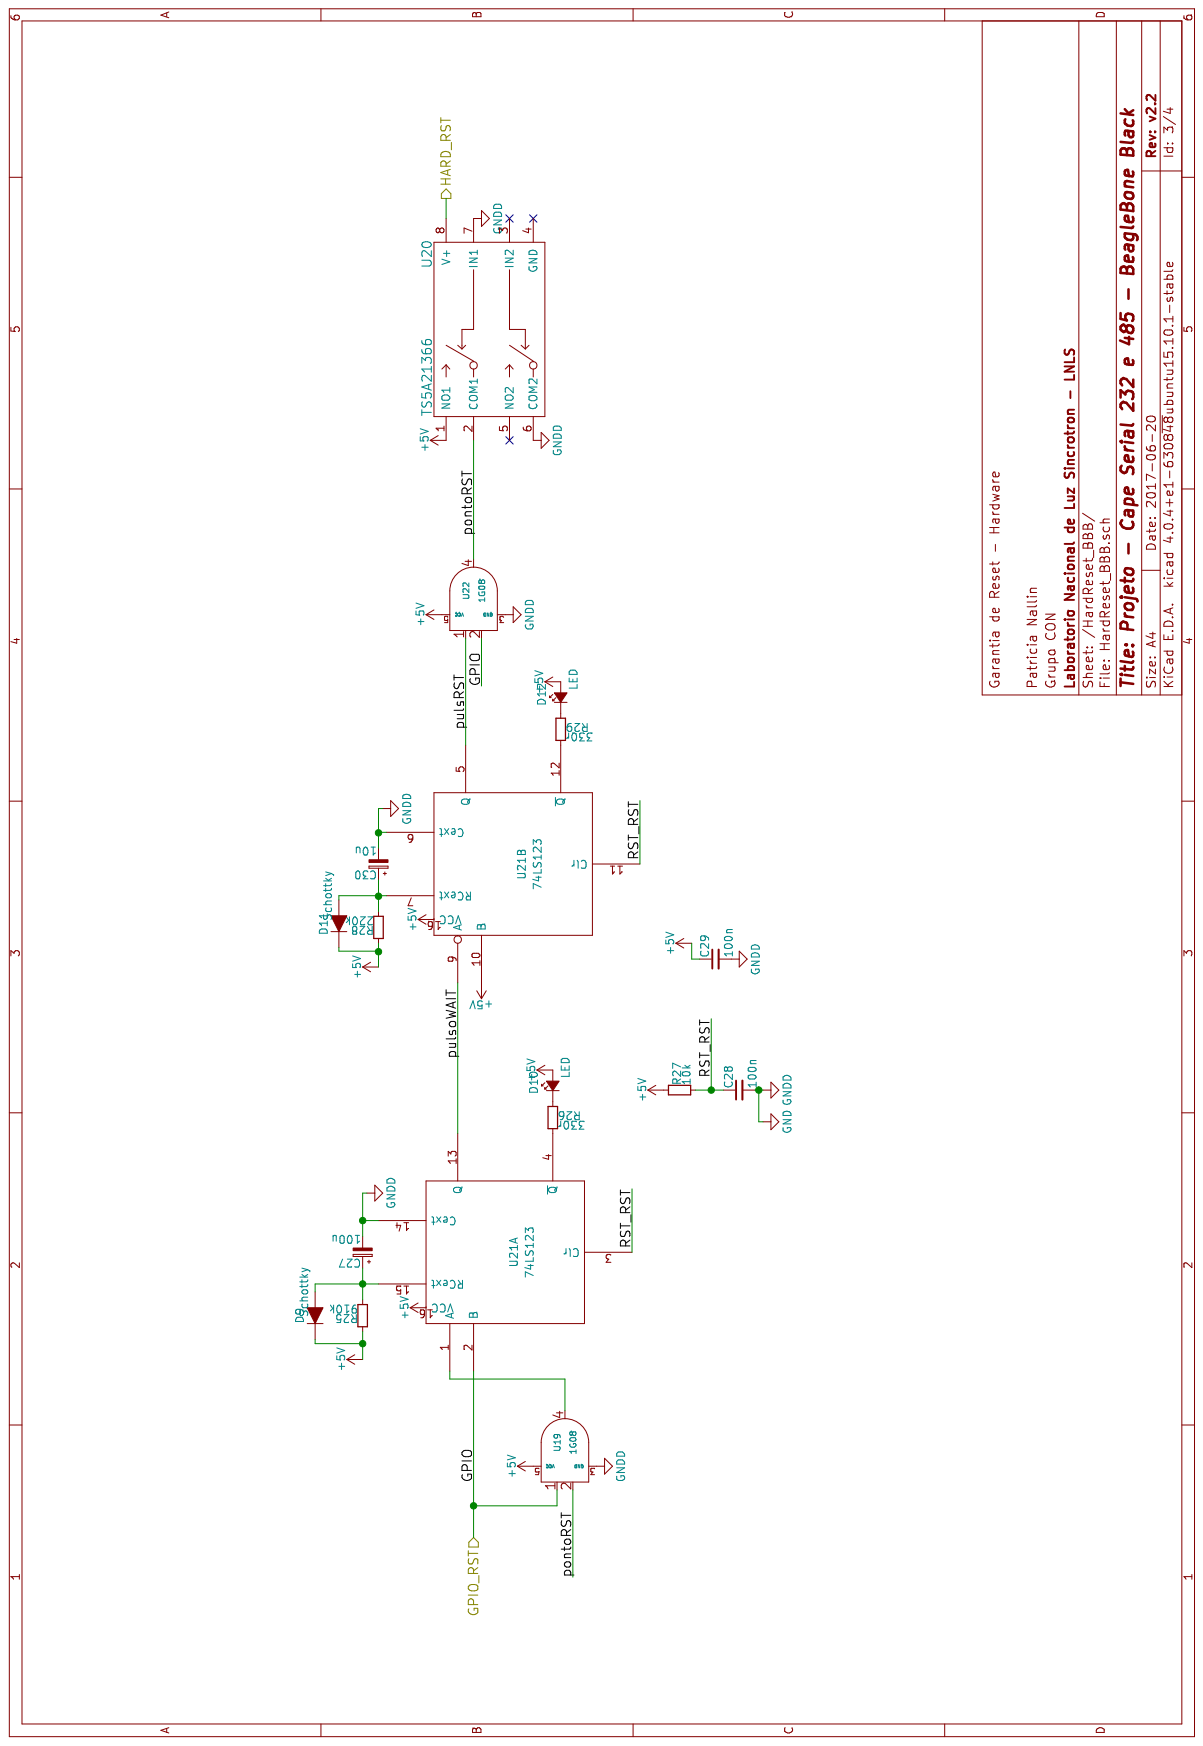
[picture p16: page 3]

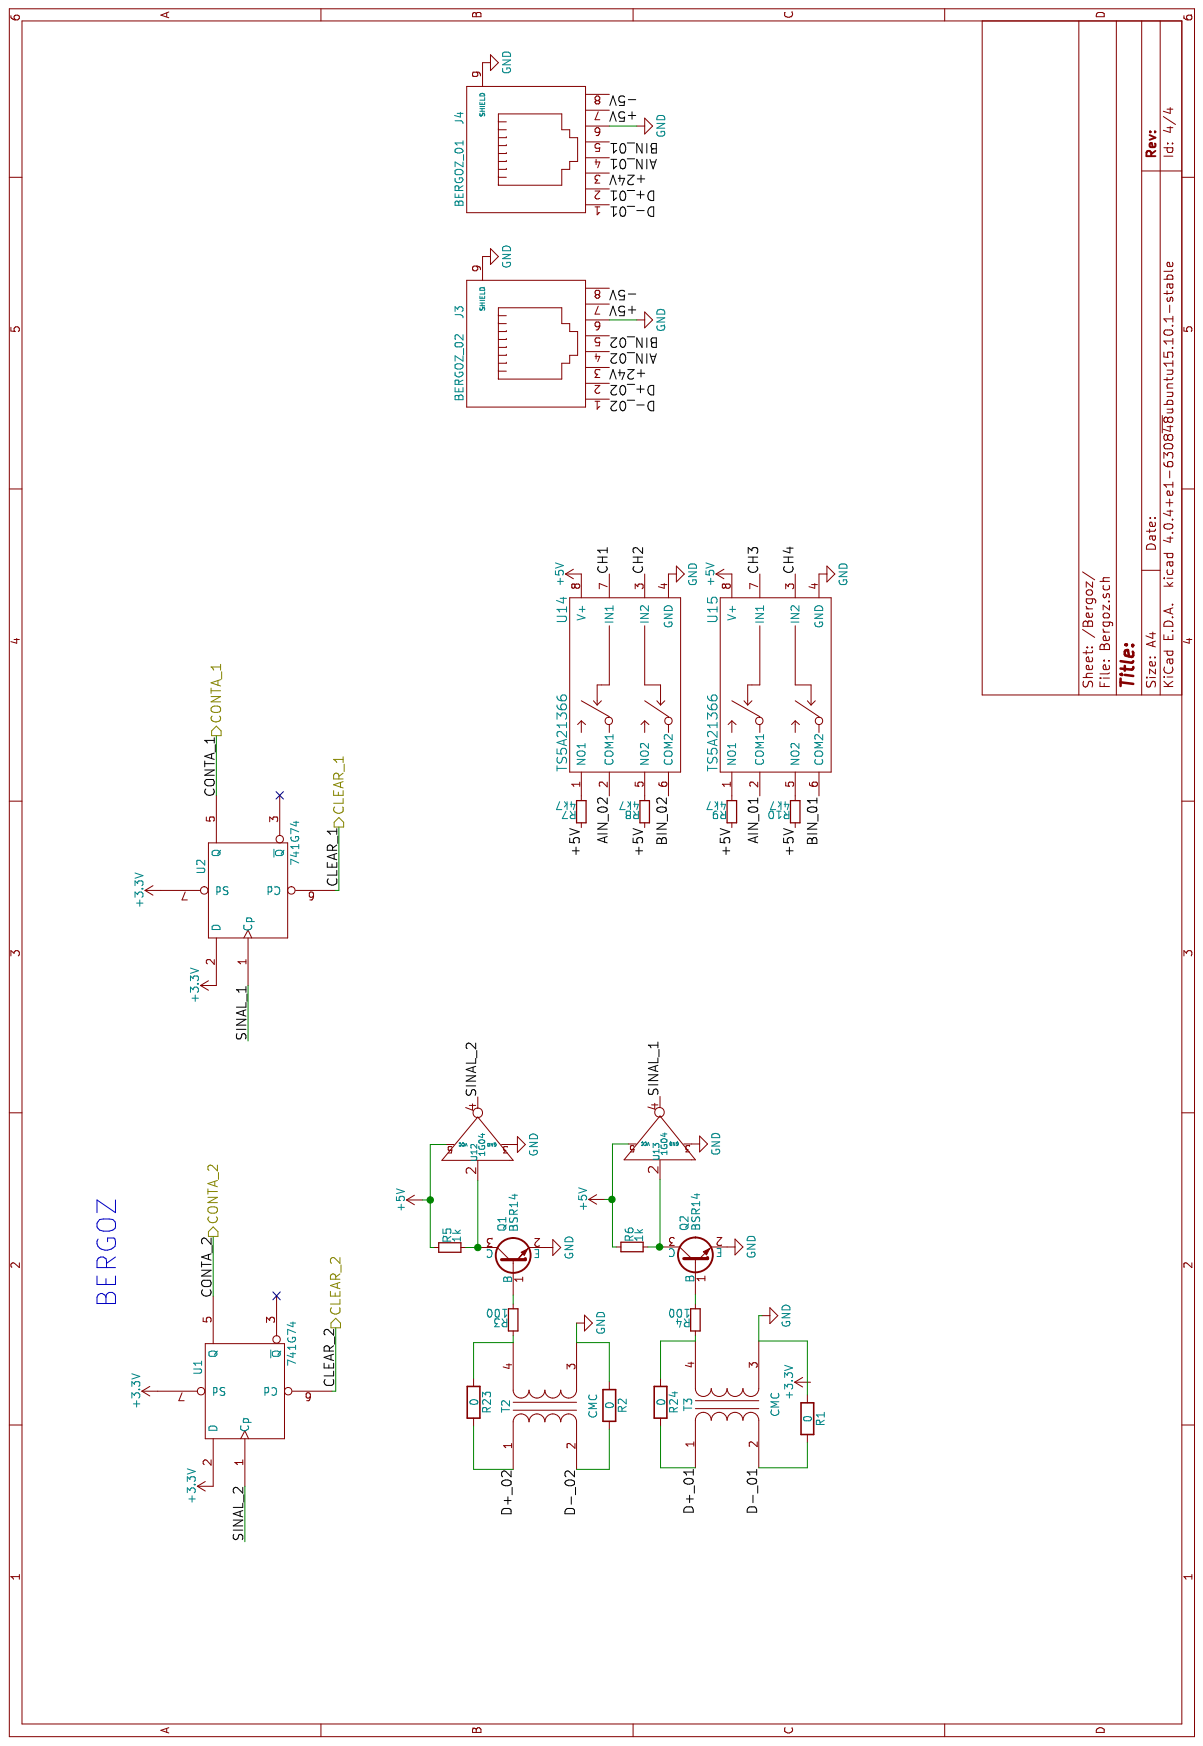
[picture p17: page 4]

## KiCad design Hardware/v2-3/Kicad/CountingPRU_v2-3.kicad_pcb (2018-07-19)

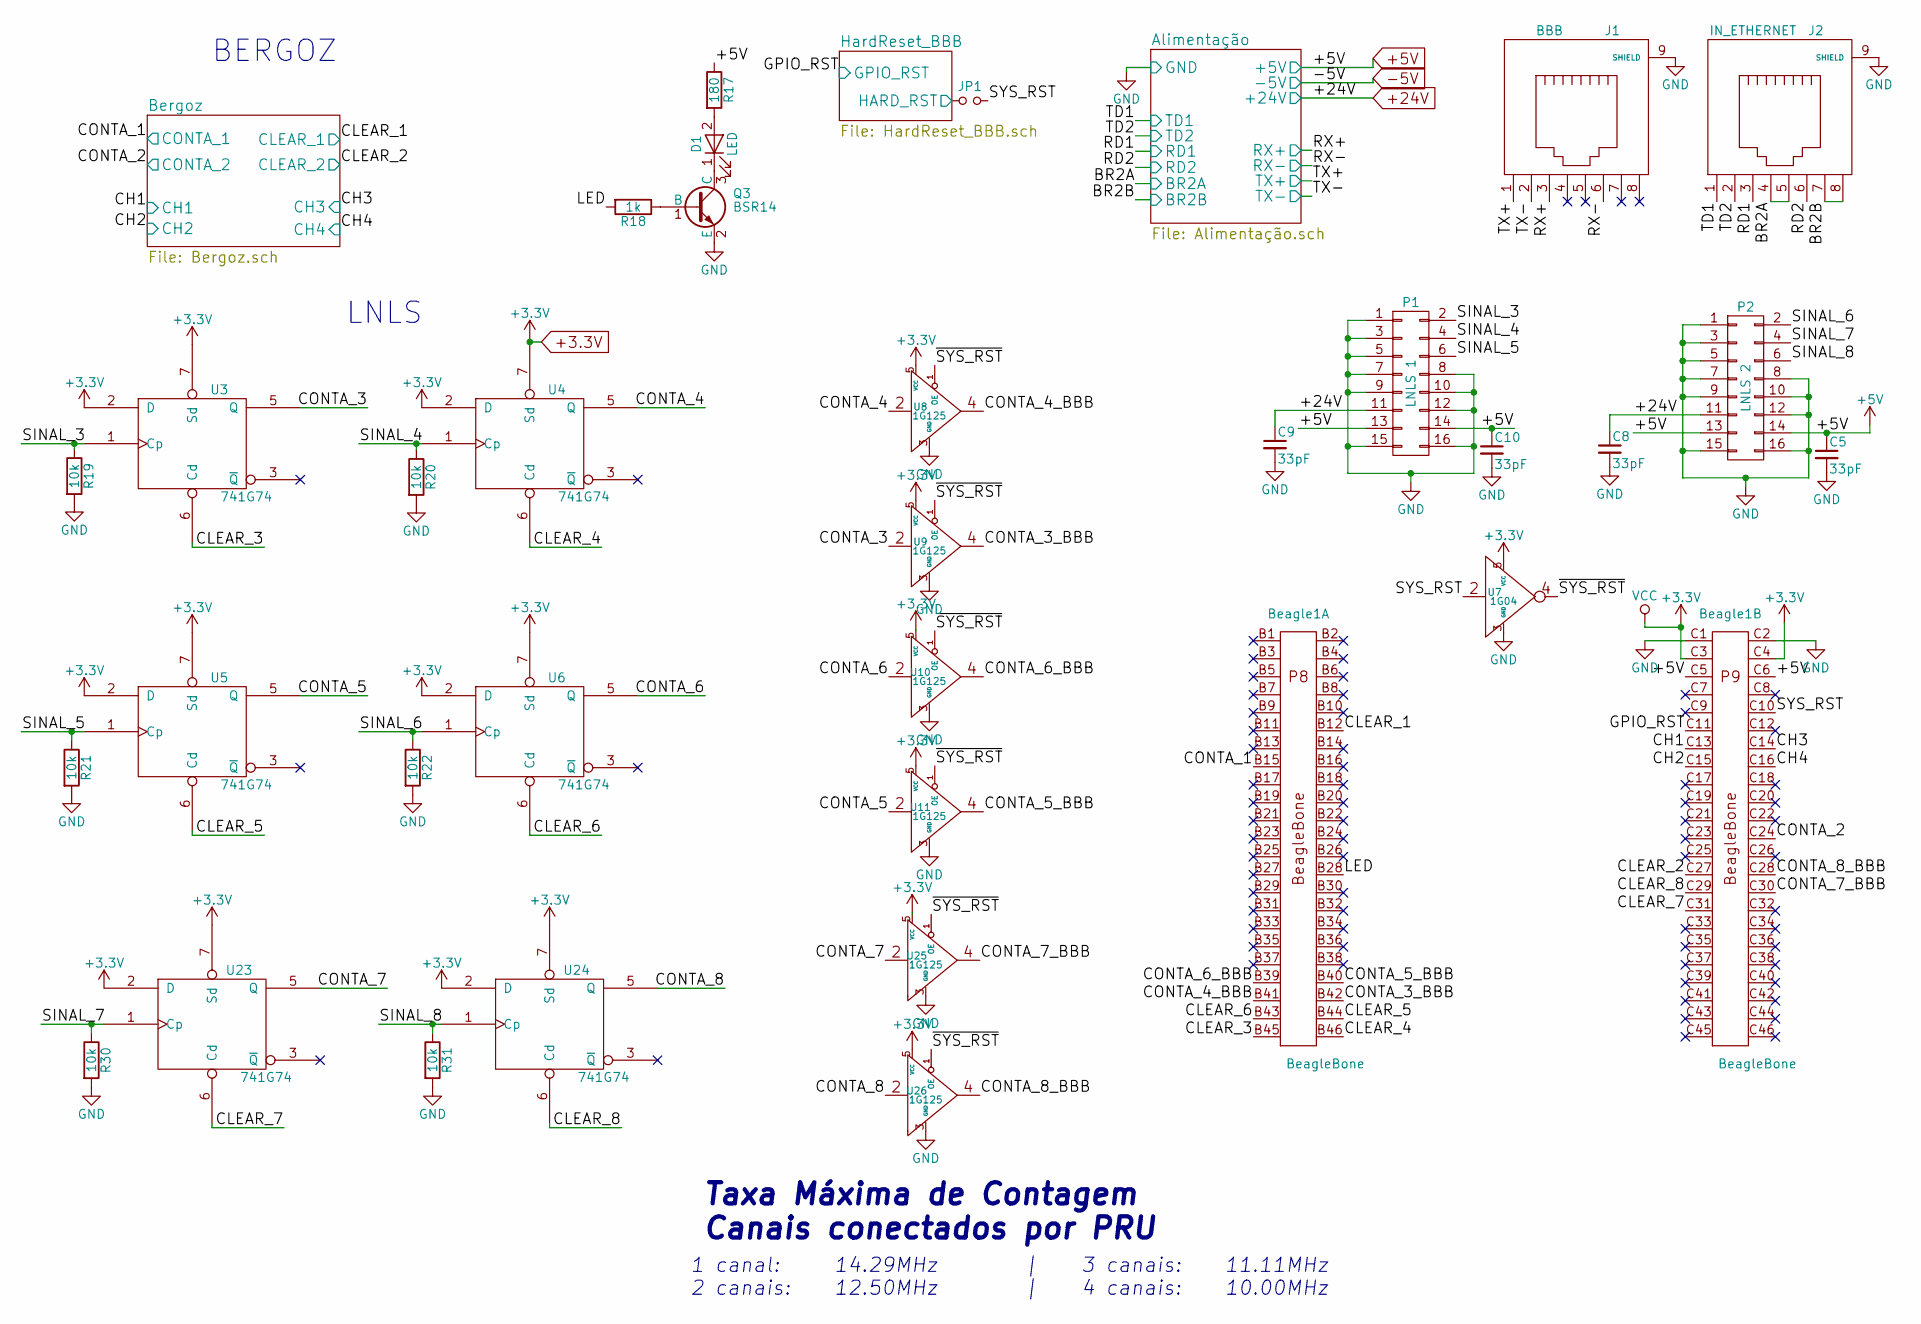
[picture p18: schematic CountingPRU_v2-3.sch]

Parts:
Beagle1: BeagleBone; BBB_Upside_Down
C5, C8, C9, C10: 33pF; C_0805
D1: LED; LED_para_painel_KINGBRIGHT
J1: BBB; RJ45-STEWART
J2: IN_ETHERNET; RJ45-STEWART
JP1: HardReset; Pin_Header_Straight_1x02_Pitch2.54mm
P1: LNLS 1; Pin_Header_Angled_2x08_Pitch1.27mm
P2: LNLS 2; Pin_Header_Angled_2x08_Pitch1.27mm
Q3: BSR14; SOT-23_Handsoldering
R17: 180; R_0805
R18: 1k; R_0805
R19, R20, R21, R22, R30, R31: 10k; R_0805
U3, U4, U5, U6, U23, U24: 741G74; TSSOP-8
U7: 1G04; SOT-353_SC-70-5_Handsoldering
U8, U9, U10, U11, U25, U26: 1G125; SOT-353_SC-70-5_Handsoldering

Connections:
+3.3V: Beagle1.C3, Beagle1.C4, U3.2 (D), U3.7 (Sd), U3.8 (VCC), U4.2 (D), U4.7 (Sd), U4.8 (VCC), U5.2 (D), U5.7 (Sd), U5.8 (VCC), U6.2 (D), U6.7 (Sd), U6.8 (VCC), U7.5 (VCC), U8.5 (VCC), U9.5 (VCC), U10.5 (VCC), U11.5 (VCC), U23.2 (D), U23.7 (Sd), U23.8 (VCC), U24.2 (D), U24.7 (Sd), U24.8 (VCC), U25.5 (VCC), U26.5 (VCC); also elsewhere on the board
+5V: Beagle1.C5, Beagle1.C6, C5.1, C10.1, P1.13, P1.14, P2.13, P2.14, R17.1; also elsewhere on the board
+24V: C8.1, C9.1, P1.11, P2.11; also elsewhere on the board
/BR2A: J2.4, J2.5; also elsewhere on the board
/BR2B: J2.7, J2.8; also elsewhere on the board
/CH1: Beagle1.C13; also elsewhere on the board
/CH2: Beagle1.C15; also elsewhere on the board
/CH3: Beagle1.C14; also elsewhere on the board
/CH4: Beagle1.C16; also elsewhere on the board
/CLEAR_1: Beagle1.B12; also elsewhere on the board
/CLEAR_2: Beagle1.C27; also elsewhere on the board
/CLEAR_3: Beagle1.B45 (C45), U3.6 (Cd)
/CLEAR_4: Beagle1.B46, U4.6 (Cd)
/CLEAR_5: Beagle1.B44, U5.6 (Cd)
/CLEAR_6: Beagle1.B43, U6.6 (Cd)
/CLEAR_7: Beagle1.C31, U23.6 (Cd)
/CLEAR_8: Beagle1.C29, U24.6 (Cd)
/CONTA_1: Beagle1.B15 (C15); also elsewhere on the board
/CONTA_2: Beagle1.C24; also elsewhere on the board
/CONTA_3: U3.5 (Q), U9.2
/CONTA_3_BBB: Beagle1.B42, U9.4
/CONTA_4: U4.5 (Q), U8.2
/CONTA_4_BBB: Beagle1.B41, U8.4
/CONTA_5: U5.5 (Q), U11.2
/CONTA_5_BBB: Beagle1.B40, U11.4
/CONTA_6: U6.5 (Q), U10.2
/CONTA_6_BBB: Beagle1.B39, U10.4
/CONTA_7: U23.5 (Q), U25.2
/CONTA_7_BBB: Beagle1.C30, U25.4
/CONTA_8: U24.5 (Q), U26.2
/CONTA_8_BBB: Beagle1.C28, U26.4
/GPIO_RST: Beagle1.C11; also elsewhere on the board
/HardReset_BBB/HARD_RST: JP1.1; also elsewhere on the board
/LED: Beagle1.B28, R18.2
/RD1: J2.3; also elsewhere on the board
/RD2: J2.6; also elsewhere on the board
/RX+: J1.3; also elsewhere on the board
/RX-: J1.6; also elsewhere on the board
/SINAL_3: P1.2, R19.1, U3.1 (Cp)
/SINAL_4: P1.4, R20.1, U4.1 (Cp)
/SINAL_5: P1.6, R21.1, U5.1 (Cp)
/SINAL_6: P2.2, R22.1, U6.1 (Cp)
/SINAL_7: P2.4, R30.1, U23.1 (Cp)
/SINAL_8: P2.6, R31.1, U24.1 (Cp)
/SYS_RST: Beagle1.C10 (B10), JP1.2, U7.2
/TD1: J2.1; also elsewhere on the board
/TD2: J2.2; also elsewhere on the board
/TX+: J1.1; also elsewhere on the board
/TX-: J1.2; also elsewhere on the board
/~SYS_RST: U7.4, U8.1 (OE), U9.1 (OE), U10.1 (OE), U11.1 (OE), U25.1 (OE), U26.1 (OE)
GND: Beagle1.C1, Beagle1.C2, C5.2, C8.2, C9.2, C10.2, J1.9 (SHIELD), J2.9 (SHIELD), P1.1, P1.3, P1.5, P1.7, P1.8, P1.9, P1.10, P1.12, P1.15, P1.16, P2.1, P2.3, P2.5, P2.7, P2.8, P2.9, P2.10, P2.12, P2.15, P2.16, Q3.2 (E), R19.2, R20.2, R21.2, R22.2, R30.2, R31.2, U3.4 (GND), U4.4 (GND), U5.4 (GND), U6.4 (GND), U7.3 (GND), U8.3 (GND), U9.3 (GND), U10.3 (GND), U11.3 (GND), U23.4 (GND), U24.4 (GND), U25.3 (GND), U26.3 (GND); also elsewhere on the board
unnamed: D1.1 (K), Q3.3 (C)
unnamed: D1.2 (A), R17.2
unnamed: Q3.1 (B), R18.1

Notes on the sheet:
LNLS
BERGOZ
1 canal: 14.29MHz | 3 canais: 11.11MHz 2 canais: 12.50MHz | 4 canais: 10.00MHz
Taxa Máxima de Contagem Canais conectados por PRU

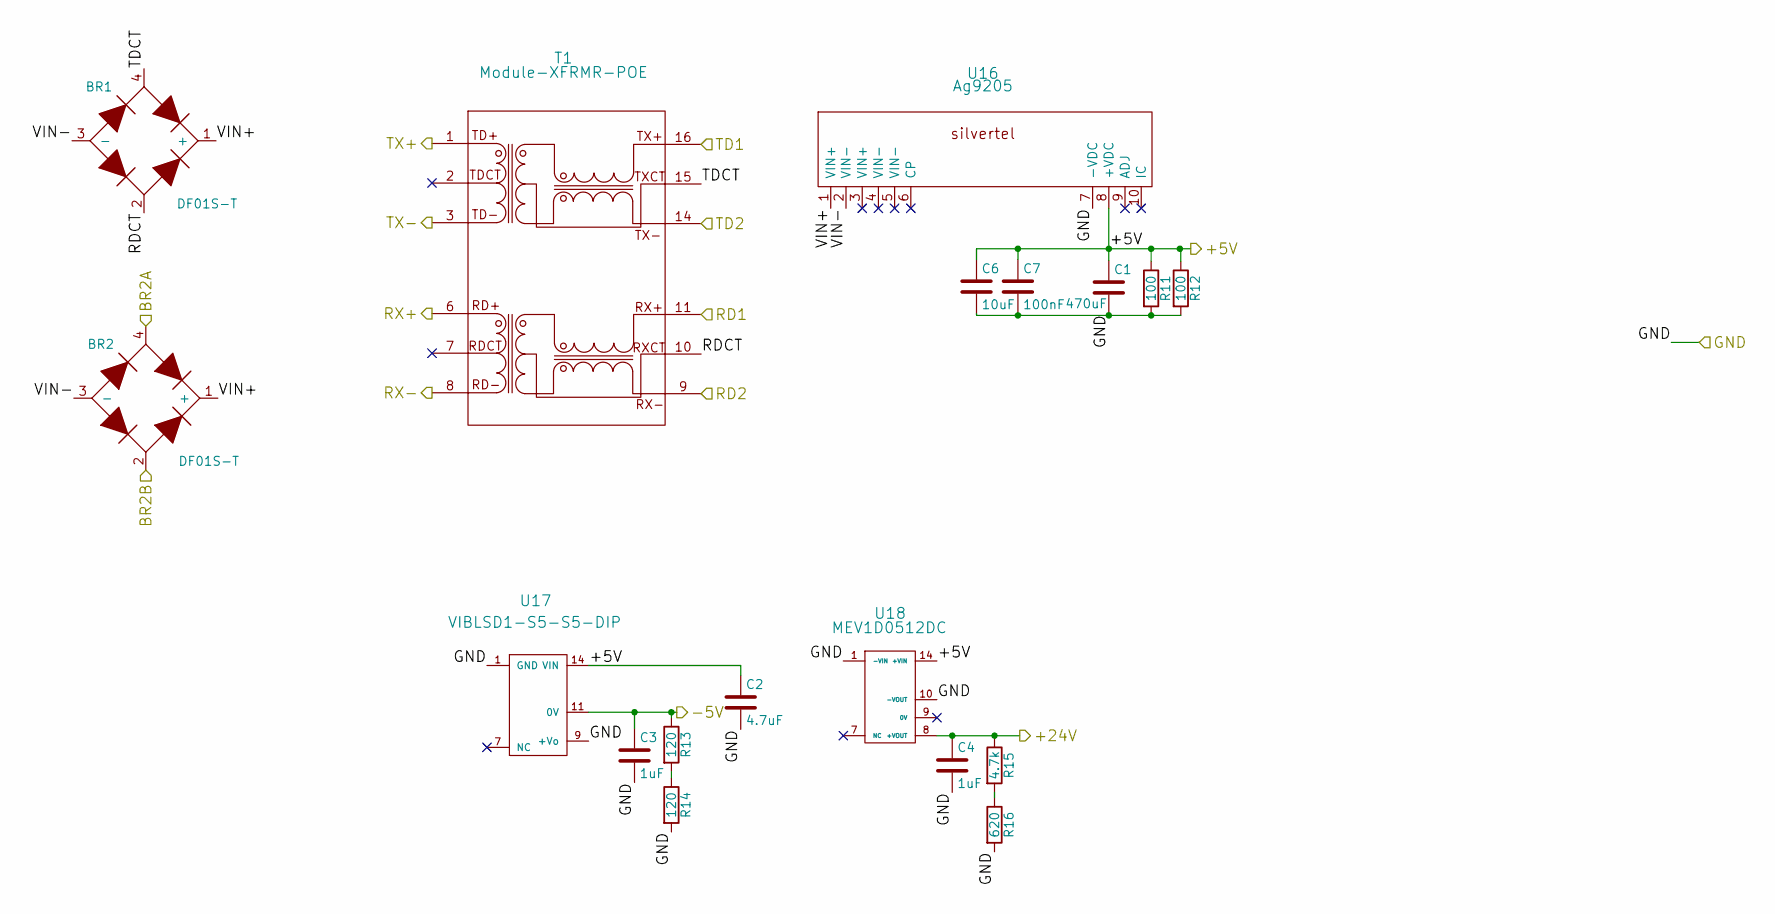
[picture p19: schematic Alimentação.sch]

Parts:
BR1, BR2: DF01S-T; RECT_BRIDGE
C1: 470uF; CP_Elec_8x5.4
C2: 4.7uF; C_0805
C3, C4: 1uF; C_0805
C6: 10uF; C_0805
C7: 100nF; C_0805
R11, R12: 100; R_MELF_MMB-0207
R13, R14: 120; R_0805
R15: 4.7k; R_0805
R16: 620; R_0805
T1: Module-XFRMR-POE; module-xfrmr-poe
U16: Ag9205; 9200-Silvertel
U17: VIBLSD1-S5-S5-DIP; VIBLSD1-DIP
U18: MEV1D0512DC

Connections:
+5V: C1.1, C2.1, C6.1, C7.1, R11.1, R12.1, U16.8 (+VDC), U17.14 (VIN), U18.14 (+VIN); also elsewhere on the board
+24V: C4.1, R15.1, U18.8 (+VOUT); also elsewhere on the board
-5V: C3.1, R13.1, U17.11 (0V); also elsewhere on the board
/Alimentação/RDCT: BR1.2, T1.10
/Alimentação/TDCT: BR1.4, T1.15
/Alimentação/VIN+: BR1.1 (+), BR2.1 (+), U16.1 (VIN+)
/Alimentação/VIN-: BR1.3 (-), BR2.3 (-), U16.2 (VIN-)
/BR2A: BR2.4; also elsewhere on the board
/BR2B: BR2.2; also elsewhere on the board
/RD1: T1.11; also elsewhere on the board
/RD2: T1.9; also elsewhere on the board
/RX+: T1.6; also elsewhere on the board
/RX-: T1.8; also elsewhere on the board
/TD1: T1.16; also elsewhere on the board
/TD2: T1.14; also elsewhere on the board
/TX+: T1.1; also elsewhere on the board
/TX-: T1.3; also elsewhere on the board
GND: C1.2, C2.2, C3.2, C4.2, C6.2, C7.2, R11.2, R12.2, R14.2, R16.2, U16.7 (-VDC), U17.1 (GND), U17.9 (+Vo), U18.1 (-VIN), U18.10 (-VOUT); also elsewhere on the board
unnamed: R13.2, R14.1
unnamed: R15.2, R16.1

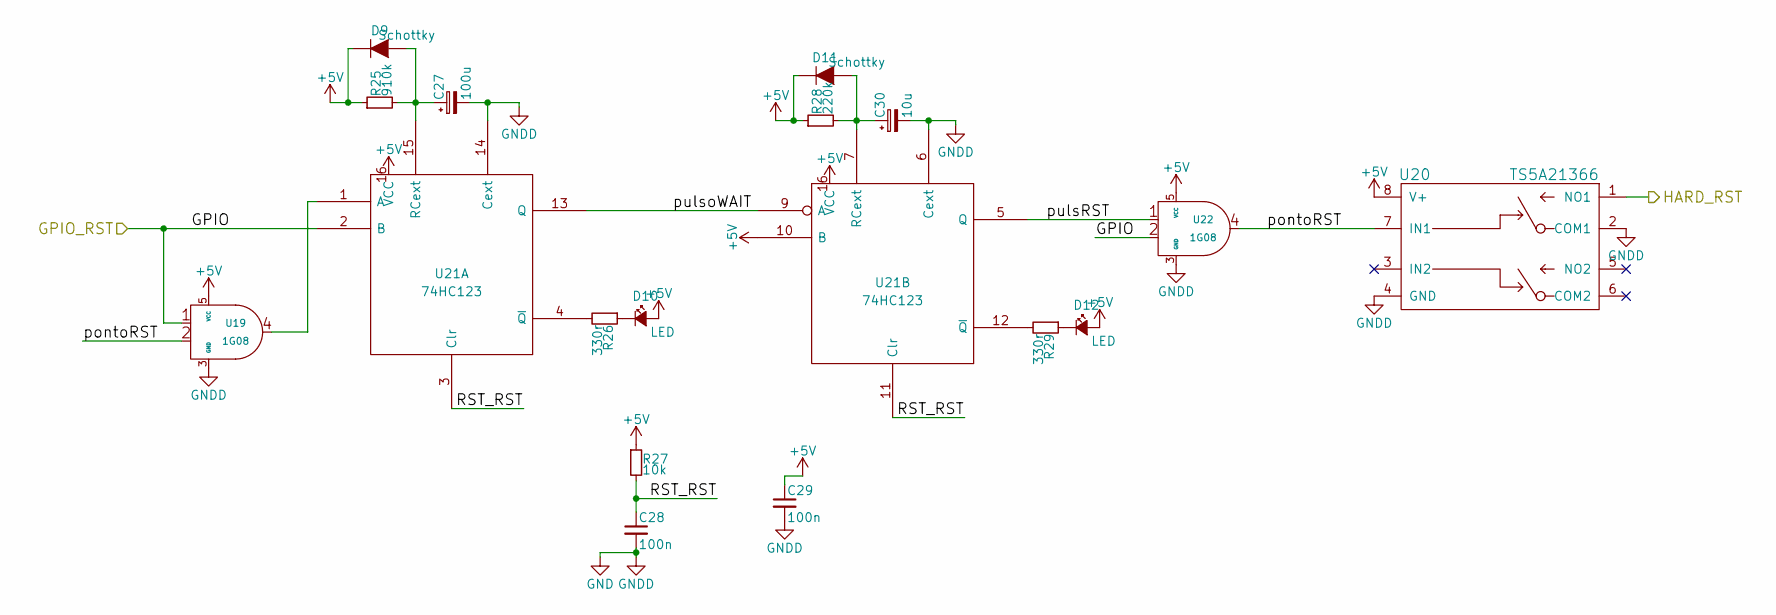
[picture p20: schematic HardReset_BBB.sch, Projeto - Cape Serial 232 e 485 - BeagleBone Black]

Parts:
C27: 100u; CP_Tantalum_Case-A_EIA-3216-18_Reflow
C28, C29: 100n; C_0805
C30: 10u; CP_Tantalum_Case-A_EIA-3216-18_Reflow
D9, D11: Schottky; D_SOD-323
D10, D12: LED; LED_0805
R25: 910k; R_0805
R26, R29: 330r; R_0805
R27: 10k; R_0805
R28: 220k; R_0805
U19, U22: 1G08; SOT-353_SC-70-5
U20: TS5A21366; VSSOP-8
U21: 74HC123; SOIC-16_3.9x9.9mm_Pitch1.27mm

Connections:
+5V: C29.1, D9.1 (K), D10.2 (A), D11.1 (K), D12.2 (A), R25.1, R27.1, R28.1, U19.5 (VCC), U20.8 (V+), U21.10 (B), U21.16 (VCC), U22.5 (VCC); also elsewhere on the board
/GPIO_RST: U19.1, U21.2 (B), U22.2; also elsewhere on the board
/HardReset_BBB/HARD_RST: U20.1 (NO1); also elsewhere on the board
/HardReset_BBB/RST_RST: C28.1, R27.2, U21.3 (Clr), U21.11 (Clr)
/HardReset_BBB/pontoRST: U19.2, U20.7 (IN1), U22.4
/HardReset_BBB/pulsRST: U21.5 (Q), U22.1
/HardReset_BBB/pulsoWAIT: U21.9 (A), U21.13 (Q)
GND: C27.2, C28.2, C29.2, C30.2, U19.3 (GND), U20.2 (COM1), U20.4 (GND), U21.6 (Cext), U21.8 (GND), U21.14 (Cext), U22.3 (GND); also elsewhere on the board
unnamed: C27.1, D9.2 (A), R25.2, U21.15 (RCext)
unnamed: C30.1, D11.2 (A), R28.2, U21.7 (RCext)
unnamed: D10.1 (K), R26.1
unnamed: D12.1 (K), R29.1
unnamed: R26.2, U21.4 (~Q)
unnamed: R29.2, U21.12 (~Q)
unnamed: U19.4, U21.1 (A)

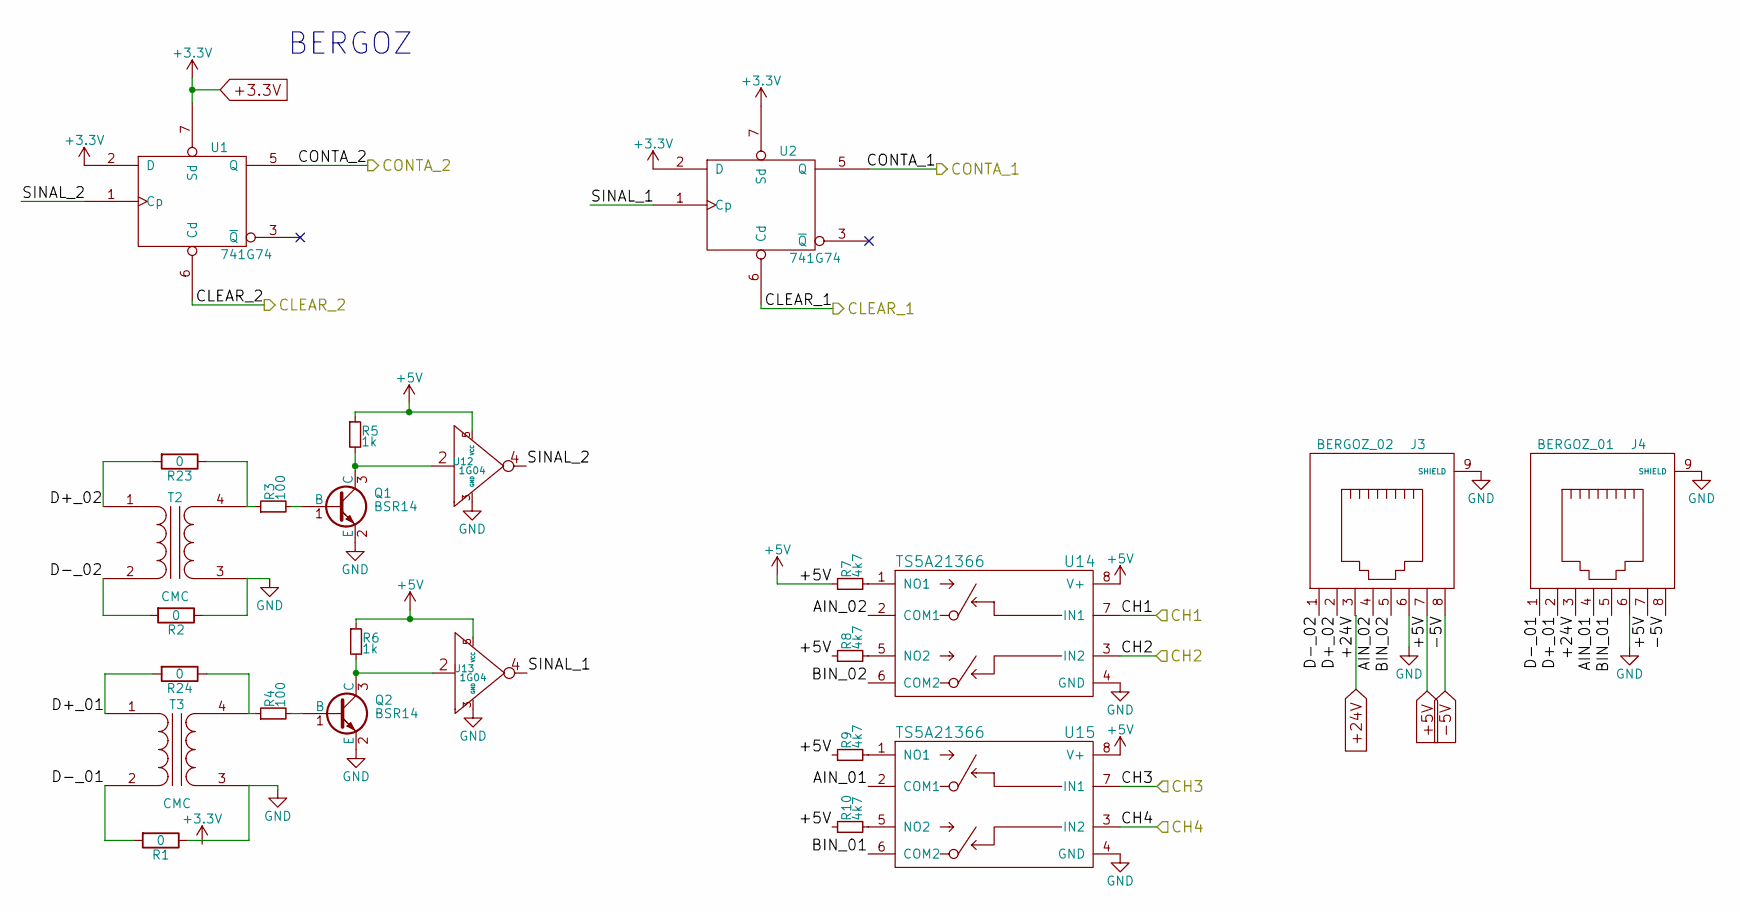
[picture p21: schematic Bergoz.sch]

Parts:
J3: BERGOZ_02; RJ45-STEWART
J4: BERGOZ_01; RJ45-STEWART
Q1, Q2: BSR14; SOT-23_Handsoldering
R1, R2, R23, R24: 0; R_0805
R3, R4: 100; R_0805
R5, R6: 1k; R_0805
R7, R8, R9, R10: 4k7; R_0805
T2, T3: CMC; Trafo_murata_SMD
U1, U2: 741G74; TSSOP-8
U12, U13: 1G04; SOT-353_SC-70-5_Handsoldering
U14, U15: TS5A21366; VSSOP-8

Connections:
+3.3V: U1.2 (D), U1.7 (Sd), U1.8 (VCC), U2.2 (D), U2.7 (Sd), U2.8 (VCC); also elsewhere on the board
+5V: J3.7, J4.7, R5.1, R6.1, R7.1, R8.1, R9.1, R10.1, U12.5 (VCC), U13.5 (VCC), U14.8 (V+), U15.8 (V+); also elsewhere on the board
+24V: J3.3, J4.3; also elsewhere on the board
-5V: J3.8, J4.8; also elsewhere on the board
/Bergoz/AIN_01: J4.4, U15.2 (COM1)
/Bergoz/AIN_02: J3.4, U14.2 (COM1)
/Bergoz/BIN_01: J4.5, U15.6 (COM2)
/Bergoz/BIN_02: J3.5, U14.6 (COM2)
/Bergoz/D+_01: J4.2, R24.2, T3.1 (AA)
/Bergoz/D+_02: J3.2, R23.2, T2.1 (AA)
/Bergoz/D-_01: J4.1, R1.2, T3.2 (AB)
/Bergoz/D-_02: J3.1, R2.2, T2.2 (AB)
/Bergoz/SINAL_1: U2.1 (Cp), U13.4
/Bergoz/SINAL_2: U1.1 (Cp), U12.4
/CH1: U14.7 (IN1); also elsewhere on the board
/CH2: U14.3 (IN2); also elsewhere on the board
/CH3: U15.7 (IN1); also elsewhere on the board
/CH4: U15.3 (IN2); also elsewhere on the board
/CLEAR_1: U2.6 (Cd); also elsewhere on the board
/CLEAR_2: U1.6 (Cd); also elsewhere on the board
/CONTA_1: U2.5 (Q); also elsewhere on the board
/CONTA_2: U1.5 (Q); also elsewhere on the board
GND: J3.6, J3.9 (SHIELD), J4.6, J4.9 (SHIELD), Q1.2 (E), Q2.2 (E), R1.1, R2.1, T2.3 (SA), T3.3 (SA), U1.4 (GND), U2.4 (GND), U12.3 (GND), U13.3 (GND), U14.4 (GND), U15.4 (GND); also elsewhere on the board
unnamed: Q1.1 (B), R3.2
unnamed: Q1.3 (C), R5.2, U12.2
unnamed: Q2.1 (B), R4.2
unnamed: Q2.3 (C), R6.2, U13.2
unnamed: R7.2, U14.1 (NO1)
unnamed: R8.2, U14.5 (NO2)
unnamed: R9.2, U15.1 (NO1)
unnamed: R10.2, U15.5 (NO2)
unnamed: R3.1, R23.1, T2.4 (SB)
unnamed: R4.1, R24.1, T3.4 (SB)

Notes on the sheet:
BERGOZ

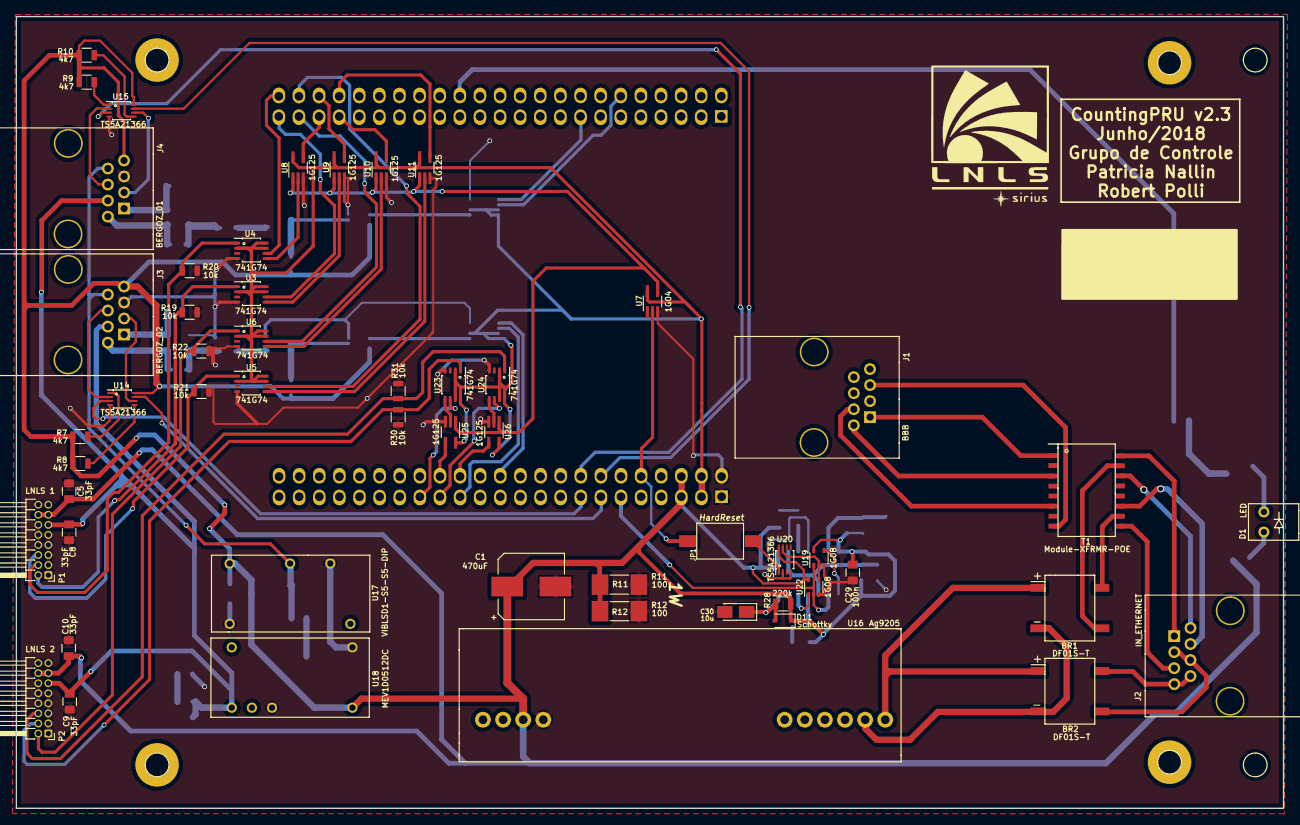
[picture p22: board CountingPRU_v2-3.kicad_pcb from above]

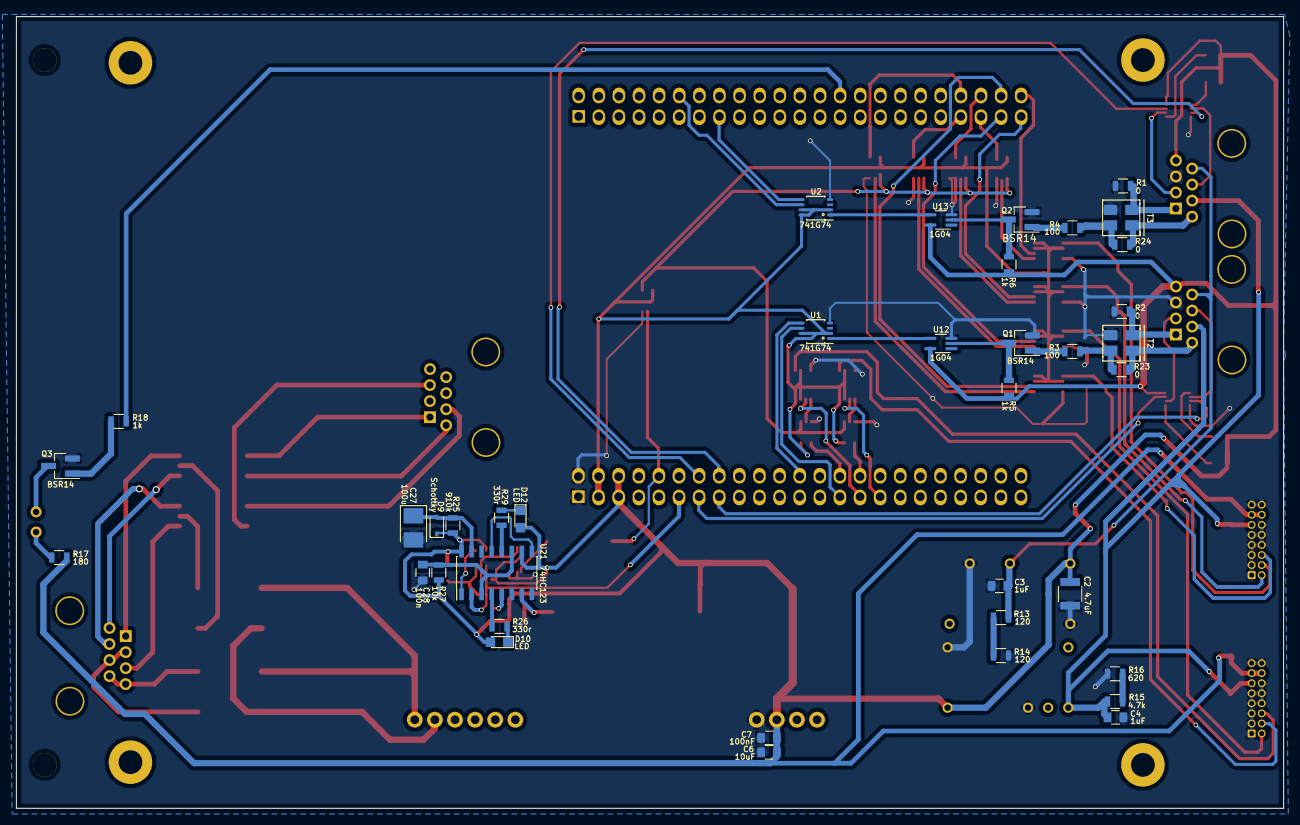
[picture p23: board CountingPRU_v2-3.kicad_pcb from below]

Board: 2 copper layers, 160.0 x 100.0 mm, 94 parts (38 on the bottom side), 92 nets.

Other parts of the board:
 : C64AC; Eurocard_template
 #2: LNLS_LOGO_Silk

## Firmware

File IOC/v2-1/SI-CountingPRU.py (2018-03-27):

#!/usr/bin/python2
# -*- coding: utf-8 -*-


# SI-SiriusBLM-PRU - Baseboard v2-1
# Software de Interface - SiriusBLM PRU-based

# Patricia H Nallin
# (Adaptado de Eduardo P Coelho)


# Modulos necessarios
from pcaspy import Driver, Alarm, Severity, SimpleServer
from Queue import PriorityQueue
import Adafruit_BBIO.GPIO as GPIO
import traceback
import threading
import time
import serial
import socket
import sys
import CountingPRU



# Configuracao dos BLMs associados a placa
BLMs = ["LNLS1", "LNLS2", "LNLS3", "LNLS4","Bergoz1", "Bergoz2"]

# Pinos Inhibit
InhA1 = "P9_14"
InhB1 = "P9_16"
InhA2 = "P9_13"
InhB2 = "P9_15"

GPIO.setup(InhA1, GPIO.OUT)
GPIO.output(InhA1, GPIO.LOW)
GPIO.setup(InhB1, GPIO.OUT)
GPIO.output(InhB1, GPIO.LOW)

GPIO.setup(InhA2, GPIO.OUT)
GPIO.output(InhA2, GPIO.LOW)
GPIO.setup(InhB2, GPIO.OUT)
GPIO.output(InhB2, GPIO.LOW)


# Define as PVs que serao servidas pelo programa
PVs = {}
for module in BLMs:
    if module == "Bergoz1" or module == "Bergoz2":
	PVs["UVX:CountingPRU:" + sys.argv[1] + ":" + module] = { "type" : "int", "unit" : "electrons per second"}
	PVs["UVX:CountingPRU:" + sys.argv[1] + ":" + module + "-InhA"] = { "type" : "enum", "enums" : ["off", "on"]}
        PVs["UVX:CountingPRU:" + sys.argv[1] + ":" + module + "-InhB"] = { "type" : "enum", "enums" : ["off", "on"]}
    else:
	PVs["UVX:CountingPRU:" + sys.argv[1] + ":" + module] = { "type" : "int", "unit" : "gama per second"}

PVs["UVX:CountingPRU:" + sys.argv[1] + ":TimeBase"] = { "type" : "int", "unit" : "seconds"}



# Inicializacao da biblioteca de contagem
CountingPRU.Init()


# Time String
def time_string():
    return(time.strftime("%d/%m/%Y, %H:%M:%S - ", time.localtime()))

# Driver EPICS para as placas contadoras SiriusBLM-CPLD
class PSDriver(Driver):

    # Construtor da classe
    def __init__(self):

        # Chama o construtor da superclasse
        Driver.__init__(self)

        # Define condicoes iniciais das variáveis EPICS de escrita
        for module in BLMs:
                self.setParam("UVX:CountingPRU:" + sys.argv[1] + ":" + module, 0)
                self.setParamStatus("UVX:CountingPRU:" + sys.argv[1] + ":" + module, Alarm.NO_ALARM, Severity.NO_ALARM)
		if module == "Bergoz1" or module == "Bergoz2":
			self.setParam("UVX:CountingPRU:" + sys.argv[1] + ":" + module + "-InhA", 0)
			self.setParam("UVX:CountingPRU:" + sys.argv[1] + ":" + module + "-InhB", 0)
			self.setParamStatus("UVX:CountingPRU:" + sys.argv[1] + ":" + module + "-InhA", Alarm.NO_ALARM, Severity.NO_ALARM)
			self.setParamStatus("UVX:CountingPRU:" + sys.argv[1] + ":" + module + "-InhB", Alarm.NO_ALARM, Severity.NO_ALARM)


        self.setParam("UVX:CountingPRU:" + sys.argv[1] + ":TimeBase", 1)
        self.setParamStatus("UVX:CountingPRU:" + sys.argv[1] + ":TimeBase", Alarm.NO_ALARM, Severity.NO_ALARM)

        # Fila de prioridade
        self.queue = PriorityQueue()

        # Objeto do tipo Event para temporizacao das leituras
        self.event = threading.Event()

        # Cria, configura e inicializa as threads
        self.process = threading.Thread(target = self.processThread)
        self.scan = threading.Thread(target = self.scanThread)

        self.process.setDaemon(True)
        self.scan.setDaemon(True)

        self.process.start()
        self.scan.start()


    # Thread que, periodicamente (duas vezes por segundo), enfileira operacao de leitura

    def scanThread(self):
        while (True):
                self.queue.put((1, ["READ_COUNTERS"]))
                self.event.wait(self.getParam("UVX:CountingPRU:" + sys.argv[1] + ":TimeBase"))



    # Thread que processa a fila de operacoes
    def processThread(self):
        # Laco que executa indefinidamente
        while (True):
            # Retira a proxima operacao da fila
            item = self.queue.get(block = True)
            item = item[1]

            # Verifica a operacao a ser realizada

            if (item[0] == "READ_COUNTERS"):

                # Operação de leitura
                # Solicita os valores - BASE DE TEMPO
                Counter = CountingPRU.Counting(self.getParam("UVX:CountingPRU:" + sys.argv[1] + ":TimeBase"))

                # Atualiza os valores das variáveis EPICS e bloco de leitura associados
                for channel in range (len(BLMs)):
                        self.setParam("UVX:CountingPRU:" + sys.argv[1] + ":" + BLMs[channel], Counter[channel])
                self.updatePVs()



    # Nao permite escrita em PVs
    def write(self, reason, value):

        if reason[-9:] == ":TimeBase":
            self.setParam(reason, value)
            self.updatePVs()
            return (True)

	# Modo Calibracao
	elif reason[-6:-1] == "1-Inh":
		if reason[-1:] == "A":
			if value:
				GPIO.output(InhA1, GPIO.HIGH)
			else:
				GPIO.output(InhA1, GPIO.LOW)

		elif reason[-1:] == "B": 
			if value:
                                GPIO.output(InhB1, GPIO.HIGH)
                        else:
                                GPIO.output(InhB1, GPIO.LOW)

		self.setParam(reason, value)
            	self.updatePVs()
            	return (True)

	elif reason[-6:-1] == "2-Inh":	
		if reason[-1:] == "A":
                        if value:
                                GPIO.output(InhA2, GPIO.HIGH)
                        else:
                                GPIO.output(InhA2, GPIO.LOW)

                elif reason[-1:] == "B":
                        if value:
                                GPIO.output(InhB2, GPIO.HIGH)
                        else:
                                GPIO.output(InhB2, GPIO.LOW)

                self.setParam(reason, value)
                self.updatePVs()
                return (True)

        else:
            return(False)



# Rotina executada quando o programa e lancado
if (__name__ == '__main__'):

    # Imprime uma mensagem inicial na tela
    sys.stdout.write("SI-SiriusBLM:PRU SiriusBLM - PRU-based\n")
    sys.stdout.write(time_string() + "Programa inicializado.\n")
    sys.stdout.flush()

    # Inicializa o servidor EPICS
    CAserver = SimpleServer()
    CAserver.createPV("", PVs)
    driver = PSDriver()

    # Laco que executa indefinidamente
    while (True):
        CAserver.process(0.1)

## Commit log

2018-01-18 Updated files and library. New SI version
    [Alimentação.sch, BOM_CountingPRU.ods, Contador-B.Adhes.gbr, Contador-B.CrtYd.gbr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]
2018-02-16 New SI and Hardware files - BaseTime via EPICS
    [Alimentação.sch]
2018-02-21 new SI, considering Bergoz calibration
2018-03-26 Updating files for 2 LNLS connector
    [Alimentação.sch, BOM_CountingPRU.ods, BOM_CountingPRU_v2-2.ods, Bergoz.sch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]
2018-03-27 IOC files added and hardware v2-2 updated
    [CountingPRU_v2-2-B.Adhes.gbr, CountingPRU_v2-2-B.CrtYd.gbr, CountingPRU_v2-2-B.Cu.gbr, CountingPRU_v2-2-B.Fab.gbr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]
2018-04-12 BOM completed
    [BOM_CountingPRU_v2-2.ods]
2018-04-17 Update hardware files
    [Alimentação.sch, Bergoz.sch, CountingPRU_v2-2.kicad_pcb, CountingPRU_v2-2.sch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]
2018-05-17 Config pins for kernel 4.14 added
    [Alimentação.sch, BOM_CountingPRU_v2-3.ods, Bergoz.sch, CountingPRU_v2-2-B.Adhes.gbr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]
2018-07-19 Updating v2-3 hardware files
    [Alimentação.sch, BOM_CountingPRU_v2-3.ods, Bergoz.sch, CountingPRU_v2-3-B.Adhes.gbr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]
2018-08-14 Production files added
    [BOM_CountingPRU_v2-3.ods]
2018-08-17 Jiga files added
    [BOM_CountingPRU_v2-3.xlsx]
2018-08-20 zip files
    [CountingPRU_v2-3-B.Adhes.gbr, CountingPRU_v2-3-B.CrtYd.gbr, CountingPRU_v2-3-B.Cu.gbr, CountingPRU_v2-3-B.Fab.gbr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]
2018-09-04 organizing files
    [CountingPRU_v2-3-B.Adhes.gbr, CountingPRU_v2-3-B.CrtYd.gbr, CountingPRU_v2-3-B.Cu.gbr, CountingPRU_v2-3-B.Fab.gbr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]
2018-09-06 Socket - BSMP protocol - version available
2020-03-16 Storing attached device serial numbers in current board
2021-09-27 Adds setup script, adds commands to config-pin
2021-10-01 Adds compatible socket script, removes redundant declarations
